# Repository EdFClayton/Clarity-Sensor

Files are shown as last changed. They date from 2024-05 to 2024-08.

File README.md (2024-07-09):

# Clarity-Sensor
Code, materials list, build instructions for a low-cost, open-source water clarity sensor 

Version 0.1
20/08/2022

Kia ora

This repository is for a water clarity sensor built as part of a PhD program in Environmental Science at the University of Auckland (Te Whare Pūtaiao, Waipapa Taumata Rau, Tāmaki Makaurau, Aotearoa).
As code, materials list and build instructions become available they will be shared here.
Real-time data will be shared when online and links will be provided.

Update 06/12/2023. Code for sensor uploaded. This is for the prototype V0.1 Draft sensor, subject to minor changes in clarity calculations and data storage. Sensor will measure beam attenuation at 563nm wavelengths for 4 different paths and then estimate beam K (diffuse attenuation) and visual clarity. Sensor also measure water temperature to provide a correction factor to the LED's (emitted light intensity varies with temperature) and two pressure sensors (one for water and another for barometric) to estimate water level.

Permission for reuse is licensed under the Creative Commons CC BY-NC-SA 4.0. You are free to copy and redistribute this material in any medium or format and to remix, transform and build upon the material. You must give appropriate credit, provide a link to the license and indicate if changes were made. You may not use the material for commercial purposes. If you remix, transform or build upon the material, you must distribute your contributions under the same license as the original.

https://creativecommons.org/licenses/by-nc-sa/4.0/ 

Ngā mihi nui

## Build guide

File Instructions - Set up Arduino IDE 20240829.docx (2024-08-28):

Set up Arduino IDE on computer

1. Download Arduino IDE application
  - https://support.arduino.cc/hc/en-us/articles/360019833020-Download-and-install-Arduino-IDE
2. Get Arduino code and libraries from GitHub (https://github.com/EdFClayton/Clarity-Sensor)
3. Go to File/Preferences
  - Add the following link into the “Additional boards manager URLs:” text box
  - https://adafruit.github.io/arduino-board-index/package_adafruit_index.json
  - Click OK

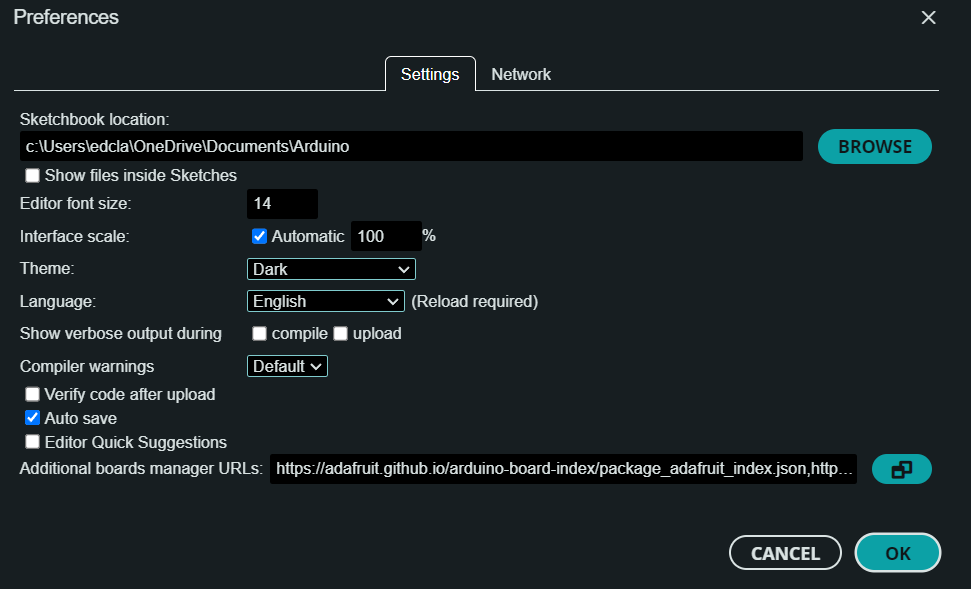
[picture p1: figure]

4. Add Adafruit board, by clicking board manager and searching for the Adafruit Feather M0 board (the board within the sensor). Select “Adafruit SAMD Boards” INSTALL button.
5. Select specific board, by clicking “Tools”>”Board”>”Adafruit SAMD Boards”>”Adafruit Feather M0 (SAMD21)”
6. Verify the code to check for issues. Pay attention to where errors occur (the app will stop when it detects an issue and highlight it).
7. Ensure that all necessary libraries are installed. To add new libraries, click the library manager tab , and search for specific libraries.
  - Unique and hard to find code libraries are on GitHub, download them as zip folders (https://github.com/EdFClayton/Clarity-Sensor/tree/main/code%20libraries)
  - To add these libraries, click “Sketch”>”Include Library”>”Add .Zip library”
  - All other libraries can be added by searching the library manager within the Arduino IDE
8. Continuing verifying code until there are no more errors.

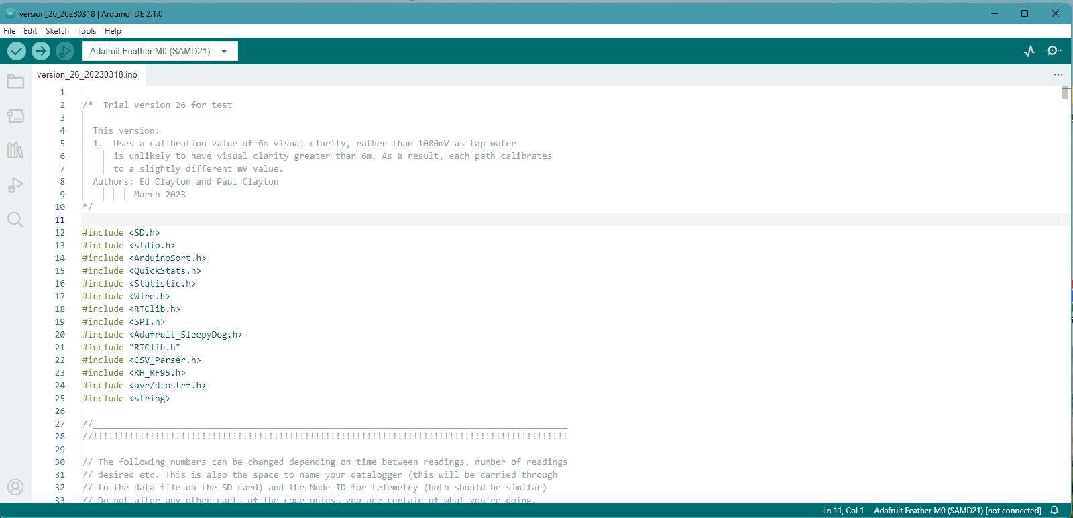
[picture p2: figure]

Library Managerager

Board Managerager

Verify

Necessary Librariesager

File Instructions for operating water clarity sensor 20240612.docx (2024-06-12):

Instructions for operating water clarity sensor

12/06/2024

Ed Clayton

The following instructions explain how to do an inspection of the sensor, clean the lenses, download data from the SD card, and then reset the sensor.

Definitions:

- Sensor board: the green PCB that the Adafruit is mounted on
- Sensor housing: the grey plastic enclosure with solar panel on
- Sensor head: the part of the sensor under the water that contains the LEDs and photodetectors
- Adafruit feather stack: the black microprocessers that contain the real time clock, LoRa radio and SD card and that the USB connects to to load code
- Arduino IDE: the software that operates the code, and reports data in real time back to the computer via the Serial Monitor (press Ctrl-Shift-M while the IDE is open)
1. When arriving at the site, the time should be noted and a photo taken of the sensor (as close to the sensor as possible without stirring up any sediment.
2. Open the sensor housing with a screwdriver or similar.
3. Connect computer to Adafruit feather via USB cable. Open Arduino IDE and press Ctrl-Shift-M to open the Serial Monitor. Sensor will output information on its operation to the computer
4. If the sensor is performing a measurement (red LED will be on for 6 seconds, off for 2 seconds for a total of 8 measurements), leave sensor to finish measurement.
5. Once sensor is finished taking measurement and goes to sleep, or if it is in sleep mode already (one brief flash every 5 seconds), press the red button and hold until the board wakes up (max 6 seconds). With the serial monitor open, the sensor will report some information, including the site name, time and date and version number. Make a note of the code version in case you have to reload code later.
6. Disconnect USB cable
7. Pull the Adafruit feather stack off the PCB. You should have in your hand the two micro boards, keep these joined together.
8. Remove SD card from the bottom micro by pushing on the card.
9. Insert SD card into card reader / laptop. Open file folder, there should be three files: CalData, CalLog and LogData. Copy the LogData file to your local drive and then close the file folder.
10. Safely eject the SD card using the computer toolbar command.
11. Reinsert SD card into the Adafruit.
12. While Adafruit is not connected to anything, clean the sensor head
13. To clean the sensor head, remove it from the water by loosening the hose clamps on the sunlight shield mount and sliding the sensor head out
14. Take photo of lenses while dirty
15. Using a cotton swab, paper towel or cleaning cloth, splash water onto the sensor head and wipe the lenses clean
16. Take photo of lenses once cleaned.
17. Slide sensor head back into sunlight shield and tighten the hose clamps. Sensor should be in exactly the same position as before it was removed, ensure that pressure sensor is facing downwards
18. Reconnect computer to the Adafruit by plugging in USV cable (don’t plug Adafruit back into sensor board yet)
19. Adafruit will start once power is provided via the USB
20. With the Arduino IDE serial monitor open, watch the information coming back from the sensor. It will report if the LoRa and SD card have been successfully started. If SD is not recognised, disconnect the USB, remove and then reinsert the SD card. This may need to be done several times and the SD card may need to be reinserted into the computer and then safely ejected to ensure correct operation (step 9).
21. If SD card and LoRa successfully start, then note the time that is reported from the sensor. If this does not match the computer time (it probably won’t), reupload the code from the Arduino IDE (right facing arrow at top left).
22. Once code is reuploaded, check that Adafruit time and date match the computer. If it does then Adafruit is ok to be reinserted into the sensor board. USB should be kept connected to the Adafruit until it is reinserted to keep power supply. When the Adafruit is successfully reinserted, a yellow LED will turn on on the Adafruit.
23. Disconnect USB and close up sensor housing
24. All done!

The following instructions set out how to calibrate the sensor. Calibrations should be conducted every 3 months

1. Get a bucket (minimum 10 litres) of clean tap water. Bucket should be cleaned before use and preferably will be black in colour with a lid to prevent as much ambient light as possible.
2. Ensure sensor head is clean and inside sunlight shield, and then put it into the bucket. Cover the bucket with a lid and/or towel to reduce ambient light as much as possible. If doing outside, make sure the bucket is out of direct light.
3. Connect sensor to computer using USB cable.
4. Open Adafruit IDE and Serial Monitor (Ctrl-Shift-M)
5. After the sensor wakes up from sleep, and before it undertakes a measurement, a prompt will appear on the Serial Monitor to do a calibration and it will countdown for 5 seconds. The red LED will flash at one second intervals while this happens.
6. Press the Red button while the countdown is happening.
7. Sensor will automatically do the calibration on all four channels. This may take around 10 – 15 minutes.
8. Sensor will calibrate each channel to an estimated 12 meters of water clarity. The ALS count for each channel will be slightly different.
9. At the end of the calibration process, the sensor will report the ALS count that each path of the sensor has calibrated to. This will be reported in a table and show how close each path is to the ideal 12m value. A warning will prompt if any path is more than 10 counts (1%) that the calibration should be redone.
  a. If a re-calibration is needed, press the reset button on the micro (small black button on the top of the Adafruit). Upload the code again (step 22 from the inspection and download instructions) so that the sensor time and date is correct, as the reset button will reset the time and date to when the Adafruit last had code loaded. After this, wait for the calibration prompt and press the red button again.
  b. If the ALS count readings look good, then nothing more is required. Unit will be calibrated

NOTE: if the sensor temperature is more than 3 or 4 degrees different from the water into which it has been placed, then as the sensor temperature changes it will affect the operation of the LED’s and photodetectors. This may cause large swings in path readings after the calibration process. As the sensor hardware (LED’s) can change brightness with even small temperature changes, this can cause erroneous clarity estimates. The tap water used for calibration should therefore be at a similar temperature to what the sensor will be put in to minimise these errors. Tap water can have ice or hot water added to adjust the temperature as needed.

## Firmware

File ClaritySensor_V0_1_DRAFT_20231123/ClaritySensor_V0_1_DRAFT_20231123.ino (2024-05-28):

/*
November 23rd, 2023

This is the draft code for a water clarity sensor developed by E Clayton for a University of Auckland PhD.

The sensor measures the attenuation of four beams of 563nm light. All beams are the same with the exception of path length.
The measurement is performed by switching on LED's and measuring the strength of transmitted light with digital ambient light sensors.
The sensor also measures water temperature, water pressure and barometric pressure to allow corrections due to environmental factors
and an understanding of clarity /  water level hysteresis. 

IMPORTANT NOTE! Any changes to this file should be recorded as a new version number IN THE FILE NAME and saved as a new sketch!
This will ensure that the version number is recorded in the logged data. 
____________________________________________________________________________________
HARDWARE
Version     Comment
------------------------------------------------------------------------------------
V0.1DRAFT   Micro: Adafruit Feather M0 RFM95 LoRA with stacked Adalogger FeatherWing
            Ambient Sensors: VEML3235SL
            LEDs: TLCPG5100
            Temperature sensor: TMP1075DGKR
            Barometric sensor: MS587302BA01-50
            Water pressure sensor: MPRLS0025PA00001A
            I2C multiplexer: TCA9548APWR
____________________________________________________________________________________
VERSION RECORD
YYYYMMDD  Number      Author        Comment
------------------------------------------------------------------------------------
20231123  V0.1DRAFT   E Clayton     Draft of sensor for testing
____________________________________________________________________________________
*/

#include <Boards.h>
#include <Firmata.h>
#include <FirmataConstants.h>
#include <FirmataDefines.h>
#include <FirmataMarshaller.h>
#include <FirmataParser.h>
#include <SD.h>
#include <stdio.h>
#include <ArduinoSort.h>
#include <QuickStats.h>
#include <Statistic.h>
#include <Wire.h>
#include <RTClib.h>
#include <SPI.h>
#include <Adafruit_SleepyDog.h>
#include "RTClib.h"
#include <CSV_Parser.h>
#include <RH_RF95.h>
#include <avr/dtostrf.h>
#include <string>
#include <VEML3235.h>
#include <TCA9548.h>
#include <Temperature_LM75_Derived.h>
#include <Adafruit_MPRLS.h>
#include <ms5837.h>

//============================================================================================
//!!!!!!!!!!!!!!!!!!!!!!!!!!!!!!!!!!!!!!!!!!!!!!!!!!!!!!!!!!!!!!!!!!!!!!!!!!!!!!!!!!!!!!!!!!!!

// The following numbers can be changed depending on time between readings, number of readings
// desired etc. This is also the space to name your datalogger (this will be carried through
// to the data file on the SD card) and the Node ID for telemetry (both should be similar). 
// Do not alter any other parts of the code unless you are certain of what you're doing. 
// WARNING! PATH LENGTHS MUST BE DECLARED IN METERS!

// number of readings to be taken, multiply by 0.8 for each measurement in seconds 
// (micro takes 800 milliseconds to read ALS sensor), then multiply by 8 for total measurement span
// (there are four paths and each path is measured twice), and then account for sensor warmup (5 seconds per path)
// i.e. (5 * 0.8 * 8) + (8 * 5) = 72 seconds.
const int numReadings = 5;    

// rename this to anything you want the Adafruit to be called (i.e. location where it will be deployed), 
// this will be stored on the SD card in the log file.
String LoggerName = "Clarity Sensor RENAME";

// site identifiers for telemetry, should reflect logger name. Need three to transmit all data. 
// NO SPACES!
char* NodeID_1 = "RENAME_a"; char* NodeID_2 = "RENAME_b"; char* NodeID_3 = "RENAME_c";  

// lengths of paths in meters to 0.2mm (use digital calipers to confirm path lengths).
float Path_A = 0.0214; float Path_B = 0.0416; float Path_C = 0.0626; float Path_D = 0.0816  ;   

// time interval in minutes between readings (default 5).
int T = 10; 

// increase the power of the LoRa radio if there are transmission problems, 
// maximum value 23 and default is 13. NOTE: THIS WILL CONSUME MORE POWER!!
int radioPower = 13;

// adjust corFactor once samples have been collected and tested for clarity via black disc. 
// CorFactor is applied in the yBD = 4.8/K equation to correct for the measurement of diffuse 
// light transmission. Minimum 5 samples over a range of clarity.
float corFactor = 1.00;

//!!!!!!!!!!!!!!!!!!!!!!!!!!!!!!!!!!!!!!!!!!!!!!!!!!!!!!!!!!!!!!!!!!!!!!!!!!!!!!!!!!!!!!!!!!!!
//============================================================================================

//Settings for Feather M0 RFM95 w/LoRa
#define RFM95_RST 4
#define RFM95_CS  8
#define RFM95_INT 3
#define RF95_FREQ 915.0   // MHz value for transmit, default 915 for Aotearoa NZ
#define LED 13

// get the file name that will include the version number
#define __FILENAME__ (strrchr(__FILE__, '\\') ? strrchr(__FILE__, '\\') + 1 : __FILE__)

// declare real time clock "rtc"
RTC_PCF8523 rtc;
// TCA multiplexer declaration called "mux" with a hexadecimal address of 70
TCA9548 mux(0x70); 
// Ambient Light Sensors (ALS) declaration "sensorRead"
VEML3235 sensorRead = VEML3235(); 
// TCA temperature sensor "readTemp" (note, TMP1075 sensor used is an evolution of LM75 sensor and library still works)
Generic_LM75 readTemp;  
// MPRLS pressure sensor declaration "waterPressure"                            
Adafruit_MPRLS waterPressure = Adafruit_MPRLS(); 
// Barometric pressure sensor declaration "baroPressure"    
static ms5837 baroPressure; 
// wd load driver instance of the radio and called it "rf95"
RH_RF95 rf95(RFM95_CS, RFM95_INT);      

unsigned long period = 905000;    // 10min delay for status message publish
unsigned long time_now = 0; 

const int CS_PIN = 10;    // pin chip select for SD card (10 is default for adafruit hardware)
const int SD_POW_PIN = 8;   // power to Adalogger featherwing
const int interrupt = 1;    // Digital pin to attach interrupt wake/calibration button to

// digital pins to control LED PWM, assigned by path (LEDx)
const int LEDa = 12;    
const int LEDb = 11;
const int LEDc = 6;
const int LEDd = 5;

// integers to hold PWM values to control full strength measurement (bright_X) and half strength measurement (bright_x)
int bright_A, bright_a;   
int bright_B, bright_b;
int bright_C, bright_c;
int bright_D, bright_d;

struct Diff   // For calibration values
{
  int diff;
} a, b, c, d;
int diff_A, diff_B, diff_C, diff_D;
int diff_a, diff_b, diff_c, diff_d;
float cal_A, cal_B, cal_C, cal_D;
float cal_a, cal_b, cal_c, cal_d;

int startTemp, endTemp; // calibration temperature values

volatile bool buttonCall;   // Volatile boolean (true/false only) that is governed by the button to calibrate or wake

Statistic statA; Statistic statB; Statistic statC; Statistic statD; Statistic stat;   // statistic arrays for sensor channels
Statistic ambientA; Statistic ambientB; Statistic ambientC; Statistic ambientD;   // statistic arrays for ambient light readings
Statistic beamK_VALUES;
Statistic beamK_values;   // statistic array for beamK_ values
Statistic FCCVALUES;
Statistic FCCvalues;    // statistic array for Fouling Corrected Clarity values

int AA, BB, CC, DD;   // integers for full strength voltage measure (integers must be used for telemetry of data)
int aA, bB, cC, dD;   // integers for half strength voltage measure
int amb_A, amb_B, amb_C, amb_D, ambientLight;   // integers for ambient light measurements
int half_A, half_B, half_C, half_D;   // integers to store full PWM - half PWM voltage value obtained during calibration
int sTemp;    // integer for temperature measurements
int mm_H20;    // integer for water level pressure
int bPressure;   // integer for barometric pressure

float LNA, LNB, LNC, LND;   // logs of readings from channels
float SENSOR_A, SENSOR_B, SENSOR_C, SENSOR_D;   // Recording readings from channels.
float SENSOR_a, SENSOR_b, SENSOR_c, SENSOR_d;
float AMBIENT_A, AMBIENT_B, AMBIENT_C, AMBIENT_D;   // Recording ambient light levels
float beamK_A, beamK_B, beamK_C, beamK_D;   // report calculated beam K (diffuse light attenuation) values
float beamK_a, beamK_b, beamK_c, beamK_d;   // report beam K for half strength measurements
float beamK_MEAN, beamK_STDDEV;
float beamK_mean, beamK_stdDev;   // floats able to hold the average and standard deviations from the statistic arrays
float yBD_A, yBD_B, yBD_C, yBD_D, yBD_Average;   // floats to hold estimtes of clarity from beam K measures
float yBD_a, yBD_b, yBD_c, yBD_d, yBD_average;
float FCC_AB, FCC_CD, FCC_AC, FCC_BD, FCC_AD, FCC_BC;   // to hold beam K (fouling corrected) values
float FCC_ab, FCC_cd, FCC_ac, FCC_bd, FCC_ad, FCC_bc;
float FCC_MEAN, FCC_STDDEV; 
float FCC_mean, FCC_stdDev;   // stats for fouling corrected values
float yBD_FC;   // float to hold estimate of clarity from fouling corrected mean
float yBD_fc;
float sensorTemp;   // float for temperature from sensor
float sensorHPA;   // float to hold hectopascal value from sensor head
float baroHPA;   // float for barometric hectopascal value from micro
float mH20;   // float to hold water level

const float VBATPIN(A7);    // pin to read battery level from
float BattV; int Bvolts;

// three different files that are written to the SD card
File CalData;   // CalData holds the PWM values for all calibrations, appended to file
File LogData;   // LogData stores all logged information from measurements, appended to file
File CalLog;    // CalLog holds the PWM sweeps performed during the last calibration only (is overwritten when a new calibration is called)

int N;    // for calibration sequences
int M;    // for index loop, indicator flashing if fitted

//___________________________________________________________________________________________
/////////////////////////////////////////////////////////////////////////////////////////////
//*******************************************************************************************
// Setup runs here. Initialises all pins, sets parameters, check sensors.
//  
// WARNING! Gets clock time from connected computer, so if no computer is connected 
// then it will reset time to last setup run when a computer was connected. Therefore,
// all data recorded to SD card will have the wrong date and time
//*******************************************************************************************
void setup() 
{
  Serial.begin(57600);
  delay(2000);

  //Flash LED for 10 seconds at 1 Hz on start up
  for (M = 1; M <= 10; M++)
  {
    digitalWrite(LED_BUILTIN, HIGH);         
    delay (500);
    digitalWrite(LED_BUILTIN, LOW);
    delay (500);
  }
  M = 1;

  // display the sensor name (i.e. the site or test)
  Serial.println("\n=====================================");
  Serial.print("\nSensor name: "); Serial.println(LoggerName); 

  // This will report the file name, which should also include the version number! See important note at start of file
  Serial.print("Version and file name: "); Serial.println(__FILENAME__);    
  delay (1000);

  // read and report battery voltage
  BattV = analogRead(VBATPIN);
  BattV *= 2;  BattV *= 3.3;  BattV /= 1024;
  Serial.print("\nBattery V = "); Serial.println(BattV);

  // ensure that the PWM has 16-bit resolution (~65,000 counts)
  analogWriteResolution(16);    

  // set all the digital pin modes
  pinMode(CS_PIN, OUTPUT);
  pinMode(SD_POW_PIN, OUTPUT);
  pinMode(LEDa, OUTPUT);
  pinMode(LEDb, OUTPUT);
  pinMode(LEDc, OUTPUT);
  pinMode(LEDd, OUTPUT);

  // turn on the chip select and SD power pins      
  digitalWrite(CS_PIN, HIGH);
  digitalWrite(SD_POW_PIN, HIGH);
  delay(1000);

  //Flash red indicator LED
  digitalWrite(LED_BUILTIN, HIGH);                                                                        
  delay (500);
  digitalWrite(LED_BUILTIN, LOW);
  delay (500);

// manual LORA radio reset
  digitalWrite(RFM95_RST, LOW);
  delay(10);
  digitalWrite(RFM95_RST, HIGH);
  delay(10);
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

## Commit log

2023-12-05 V 0.1 Draft
    Draft sensor code. Still subject to minor changes in calculating clarity and data storage
2023-12-06 Upload of PCB files
    Altium PCB file outputs (gerber, NC Drill files) and schematics uploaded
    [ClarityMezzanine_V2.SchDoc, FarBreakout.SchDoc, NearBreakout.SchDoc, PressureSensor.SchDoc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]
2023-12-06 Non standard code libraries update
    Code libraries that are not common to arduino or adafruit have been uploaded
2024-06-12 June 2024 instructions
    Upload of supporting documents, how to download and install Arduino IDE, code and libraries, and basic use of sensor including calibration
2024-08-28 Update to Arduino installation instructions
